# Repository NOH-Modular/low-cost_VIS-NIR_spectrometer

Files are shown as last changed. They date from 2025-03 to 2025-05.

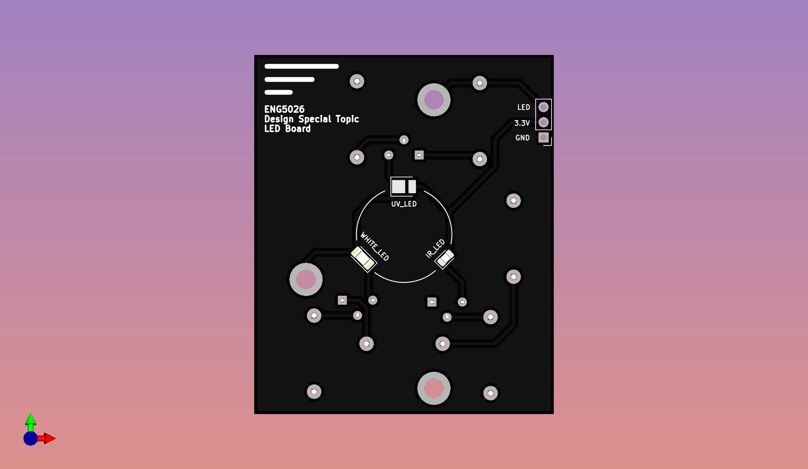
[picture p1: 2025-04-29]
HARDWARE/Embedded-Board/PICTURES/6-LED-BOARD-top.jpg

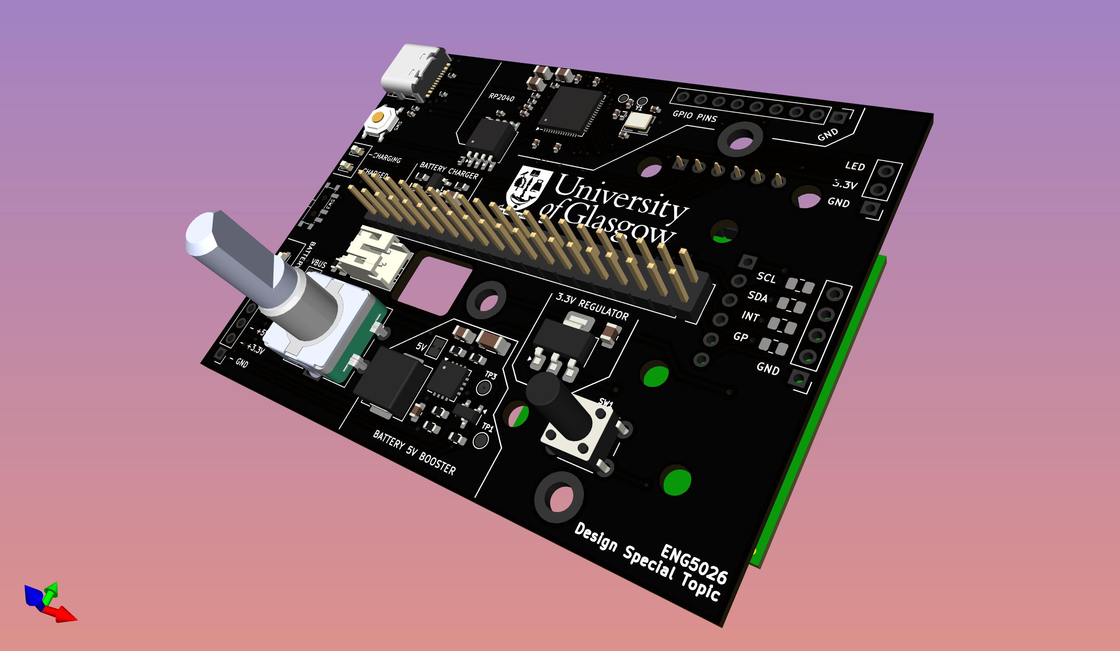
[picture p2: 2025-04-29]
HARDWARE/Embedded-Board/PICTURES/3-Embedded-Board-side.jpg

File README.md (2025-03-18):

# Low Cost VIS/NIR Spectrometer
We are a team of three students as part of Glasgow University's ENG5026 Design Special Topic 5. This class puts students in groups to initially design a proof of concept and ultimately a product in collaboration with research taking place at the University.

We aim to design a miniaturised, low-cost visible light and near-infrared spectrometer in a handheld form-factor to analyse fruit ripeness and other VIS/NIR applications including use in schools and universities. Existing products are found in the range of between £400-1000 and we aim to produce an alternative which will be more affordable and accessible.

Currently, the project consists of a custom RP2040 microcontroller board with an e-paper display to minimise power draw. The spectral sensing will use AMS-OSRAM's spectral sensor chips which has shown positive results in testing but in order to provide a more robust and elegant solution, additional funding will allow us to experiment with better sensors. The AS7265x triad sensors will give the widest possible range of sensing while still being affordable to the end user.

As well as being low-cost, it is an aim of the project to achieve long battery life for portable use. This is why low-power design such as battery management and an e-paper display has been at the forefront of component choice.

The final output (a PCB with surface-mount components pre-assembled) will be very low-cost, but we require funding for prototyping and testing various spectrometer chips, battery management, microcontrollers, and LEDs.

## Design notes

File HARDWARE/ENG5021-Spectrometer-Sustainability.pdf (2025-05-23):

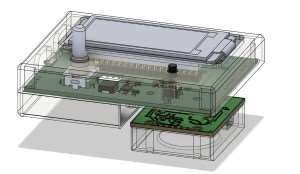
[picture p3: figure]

ENG5021-Spectrometer

3

Product name

Product life (years)

### Summary:

## Eco Audit Report

Country of use | Europe

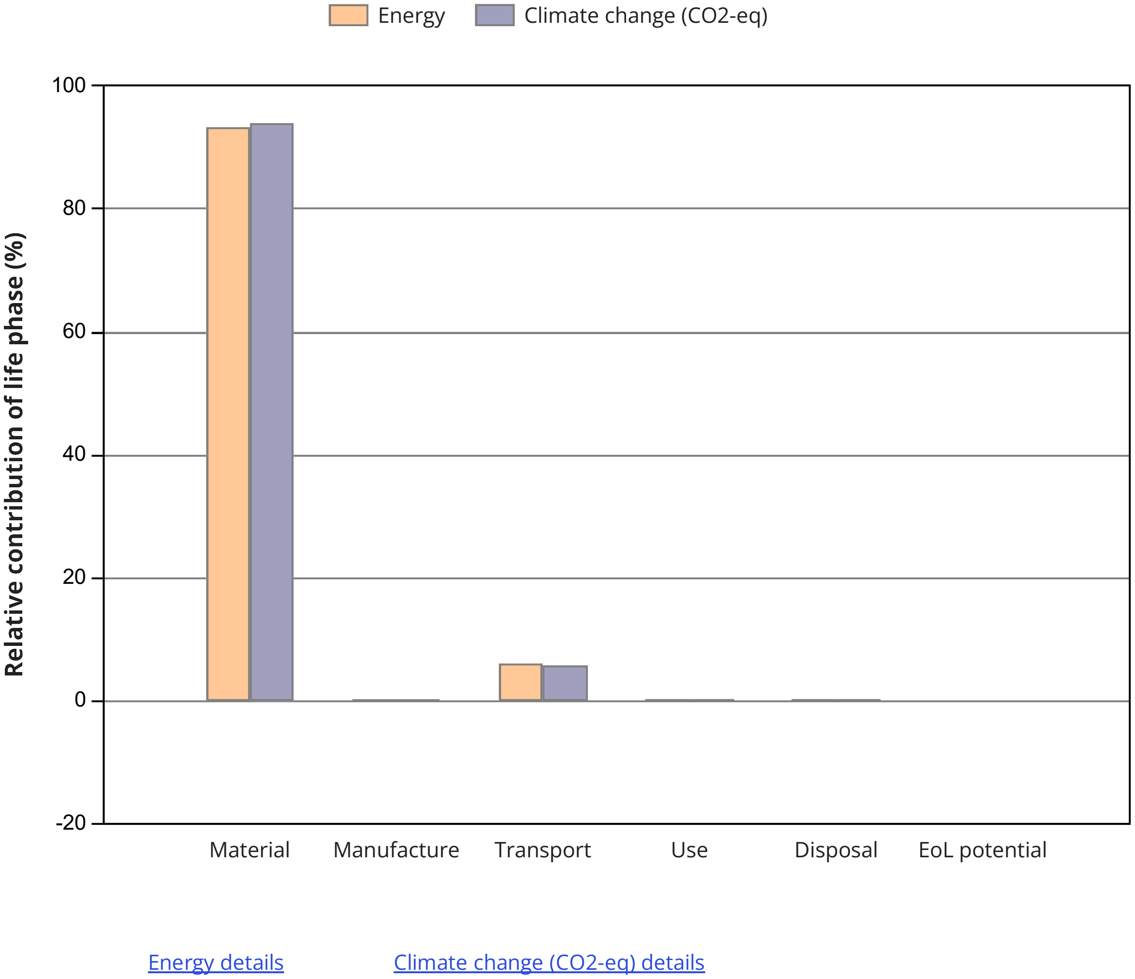
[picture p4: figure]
Material; Manufacture; Transport; Use; Disposal; EoL potential; Energy; Climate change (CO2-eq); Energy details; Climate change (CO2-eq) details

See notes on precision and data sources.

NOTE: Differences of less than 20% are not usually significant. 19-May-25

Page 1 / 10

Phase | Energy (MJ) | Energy (%) | Climate change (CO2-eq) (kg) | Climate change (CO2-eq) (%)
Material | 1.09e+03 93.5 82.3 0.148 0.0 0.0111 72.7 6.2 5.11 3.46 0.3 0.12 0.0892 0.0 0.00624 1.17e+03 100 87.6 | | | 94.0
Manufacture | | | | 0.0
Transport | | | | 5.8
Use | | | | 0.1
Disposal | | | | 0.0
Total (for first life) | | | | 100
End of life potential | 0 | | 0

Report generated by Granta EduPack 2024 R1 © 2024 ANSYS, Inc. or its

affiliated companies. All rights reserved. | 19-May-25 Page 2 / 10

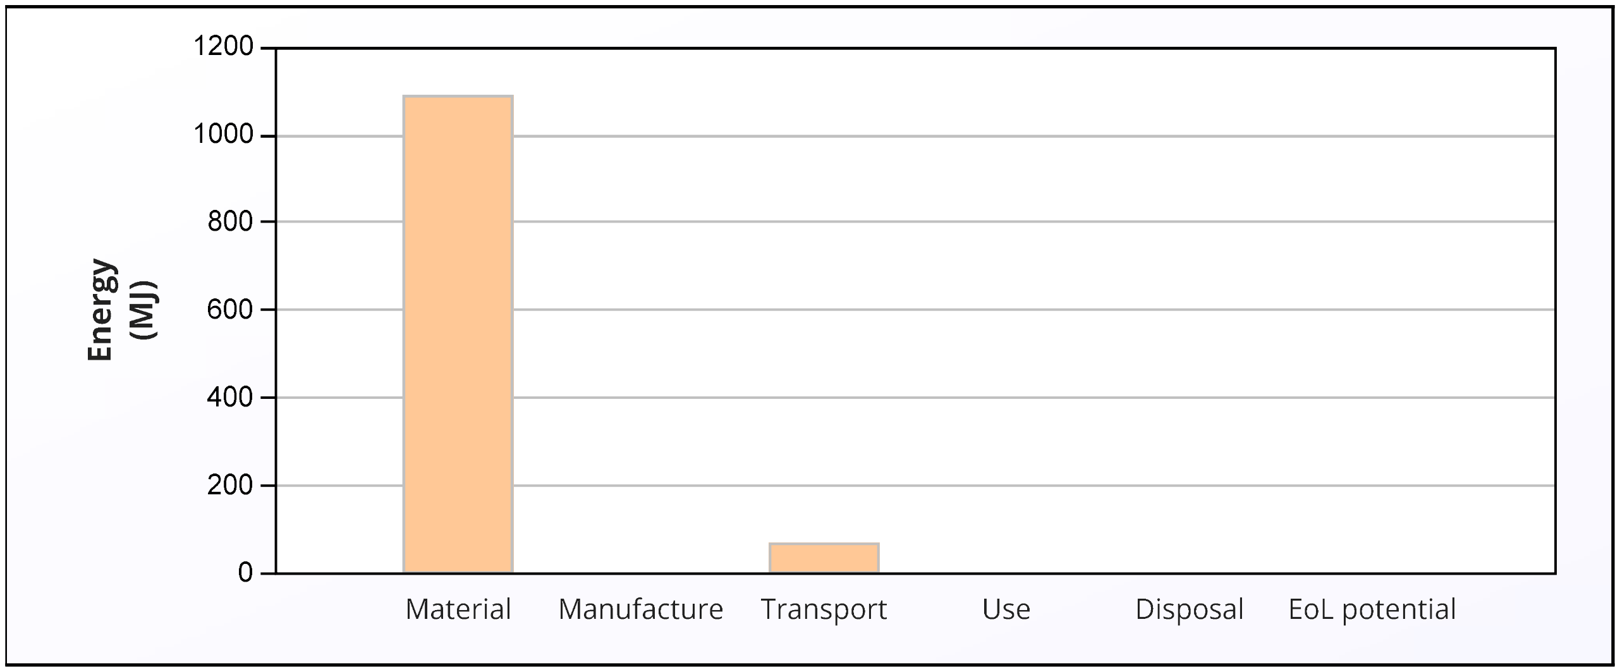
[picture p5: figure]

| Energy (MJ/year)
Equivalent annual environmental burden (averaged over 3 year product life): | 389

### Summary Energy Analysis

## Eco Audit Report

### Material:

Component | Material | Recycled content* (%) | Part mass (kg) | Qty. | Total mass (kg) | Energy (MJ) | %
Spectrometer Board | Small (hand held) electronic devices Virgin (0%) 0.3 1 0.3 8.5e+02 Small (hand held) electronic devices Virgin (0%) 0.04 1 0.04 1.1e+02 Li-Ion, rechargeable battery (for laptops) Virgin (0%) 0.016 1 0.016 15 Small (hand held) electronic devices Virgin (0%) 0.04 1 0.04 1.1e+02 PLA (general purpose) Virgin (0%) 0.025 1 0.025 1.4 | | | | | | 77.8
LED Board | | | | | | | 10.4
Rechargeable Battery | | | | | | | 1.4
Sensor PCB | | | | | | | 10.4
Plastic Enclosure | | | | | | | 0.1
Total | | | | 5 | 0.42 | 1.1e+03 | 100

## Detailed breakdown of individual life phases

Summary

*Typical: Includes 'recycle fraction in current supply'
***User-defined material

Report generated by Granta EduPack 2024 R1 © 2024 ANSYS, Inc. or its

Page 3 / 10

Manufacture: | Summary
Component | Process | Amount processed | Energy (MJ) | %
Plastic Enclosure | Polymer extrusion | 0.025 kg | 0.15 | 100.0
Total | | | 0.15 | 100

### Transport:

Breakdown by transport stage
Stage name | Transport type | Distance (km) | Energy (MJ) | %
LED/Spectrometer PCB | Aircraft, long haul belly-freight 8e+03 41 Aircraft, long haul belly-freight 6e+03 30 Truck 3.5-7.5t, EURO 3 4.4e+02 1.6 | | | 55.9
Encoder/Sensor PCB | | | | 41.9
RS - Components | | | | 2.2
Total | | 1.4e+04 | 73 | 100
Component | Mass (kg) | Energy (MJ) | %
Spectrometer Board | 0.3 52 0.04 6.9 0.016 2.8 0.04 6.9 0.025 4.3 | | 71.2
LED Board | | | 9.5
Rechargeable Battery | | | 3.9
Sensor PCB | | | 9.5
Plastic Enclosure | | | 5.9
Total | 0.42 | 73 | 100

Breakdown by components

Summary

Report generated by Granta EduPack 2024 R1 © 2024 ANSYS, Inc. or its

Page 4 / 10

### Use:

Mode | Energy
| (MJ) | %
Static | 3.5 | 100.0
Mobile | 0
Total | 3.5 | 100

Relative contribution of static and mobile modes

Energy input and output type | Electric to thermal
Country of use | Europe
Power rating (W) 0.7
Usage (hours per day) | 2
Usage (days per year) | 80
Product life (years) | 3

Static mode

Summary

### Disposal:

Component | End of life option | Energy (MJ) | %
Spectrometer Board | Landfill 0.06 Landfill 0.008 Downcycle 0.0082 Landfill 0.008 Landfill 0.005 | | 67.3
LED Board | | | 9.0
Rechargeable Battery | | | 9.2
Sensor PCB | | | 9.0
Plastic Enclosure | | | 5.6
Total | | 0.089 | 100

Summary

Component | End of life
option

Energy
(MJ) | %
Spectrometer Board | Landfill | 0
LED Board | Landfill | 0
Rechargeable Battery | Downcycle | 0
Sensor PCB | Landfill | 0
Plastic Enclosure | Landfill | 0
Total | 0 | 100

### EoL potential:

Report generated by Granta EduPack 2024 R1 © 2024 ANSYS, Inc. or its

Page 5 / 10

Notes: | Summary

Report generated by Granta EduPack 2024 R1 © 2024 ANSYS, Inc. or its

Page 6 / 10

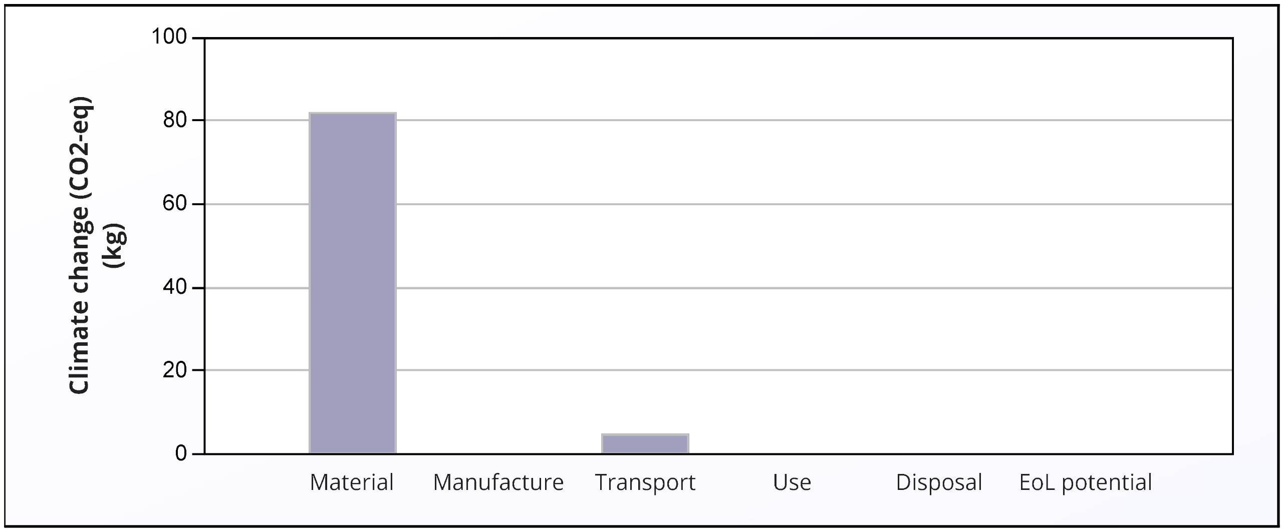
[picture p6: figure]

### Material:

Component | Material | Recycled content* (%) | Part mass (kg) | Qty. | Total mass (kg) | Climate change (CO2-eq) (kg) | %
Spectrometer Board | Small (hand held) electronic devices Virgin (0%) 0.3 1 0.3 64 Small (hand held) electronic devices Virgin (0%) 0.04 1 0.04 8.5 Li-Ion, rechargeable battery (for laptops) Virgin (0%) 0.016 1 0.016 1.7 Small (hand held) electronic devices Virgin (0%) 0.04 1 0.04 8.5 PLA (general purpose) Virgin (0%) 0.025 1 0.025 0.071 | | | | | | 77.3
LED Board | | | | | | | 10.3
Rechargeable Battery | | | | | | | 2.0
Sensor PCB | | | | | | | 10.3
Plastic Enclosure | | | | | | | 0.1
Total | | | | 5 | 0.42 | 82 | 100

## Detailed breakdown of individual life phases

Summary

*Typical: Includes 'recycle fraction in current supply'
***User-defined material
| CO2 (kg/year)
Equivalent annual environmental burden (averaged over 3 year product life): | 29.2

### Summary Climate Change (CO2-eq) Analysis

## Eco Audit Report

Report generated by Granta EduPack 2024 R1 © 2024 ANSYS, Inc. or its

Page 7 / 10

### Transport:

Breakdown by transport stage
Stage name | Transport type | Distance (km) | Climate change (CO2-eq) (kg) | %
LED/Spectrometer PCB | Aircraft, long haul belly-freight 8e+03 2.9 Aircraft, long haul belly-freight 6e+03 2.1 Truck 3.5-7.5t, EURO 3 4.4e+02 0.11 | | | 55.9
Encoder/Sensor PCB | | | | 42.0
RS - Components | | | | 2.1
Total | | 1.4e+04 | 5.1 | 100
Component | Mass (kg) | Climate change (CO2-eq) (kg) | %
Spectrometer Board | 0.3 3.6 0.04 0.49 0.016 0.2 0.04 0.49 0.025 0.3 | | 71.2
LED Board | | | 9.5
Rechargeable Battery | | | 3.9
Sensor PCB | | | 9.5
Plastic Enclosure | | | 5.9
Total | 0.42 | 5.1 | 100

Breakdown by components

Summary

Manufacture: | Summary
Component | Process | Amount processed | Climate change (CO2-eq) (kg) | %
Plastic Enclosure | Polymer extrusion | 0.025 kg | 0.011 | 100.0
Total | | | 0.011 | 100

Report generated by Granta EduPack 2024 R1 © 2024 ANSYS, Inc. or its

Page 8 / 10

### Disposal:

Component | End of life option | Climate change (CO2-eq) (kg) | %
Spectrometer Board | Landfill 0.0042 Landfill 0.00056 Downcycle 0.00057 Landfill 0.00056 Landfill 0.00035 | | 67.3
LED Board | | | 9.0
Rechargeable Battery | | | 9.2
Sensor PCB | | | 9.0
Plastic Enclosure | | | 5.6
Total | | 0.0062 | 100

Summary

Component | End of life
option

Climate
change
(CO2-eq)
(kg)

%

Spectrometer Board | Landfill | 0
LED Board | Landfill | 0
Rechargeable Battery | Downcycle | 0
Sensor PCB | Landfill | 0
Plastic Enclosure | Landfill | 0
Total | 0 | 100

### EoL potential:

### Use:

Mode | Climate change (CO2-eq)
| (kg) | %
Static | 0.12 | 100.0
Mobile | 0
Total | 0.12 | 100

Relative contribution of static and mobile modes

Energy input and output type | Electric to thermal
Country of use | Europe
Power rating (W) 0.7
Usage (hours per day) | 2
Usage (days per year) | 80
Product life (years) | 3

Static mode

Summary

Report generated by Granta EduPack 2024 R1 © 2024 ANSYS, Inc. or its

Page 9 / 10

Notes: | Summary

Report generated by Granta EduPack 2024 R1 © 2024 ANSYS, Inc. or its

Page 10 / 10

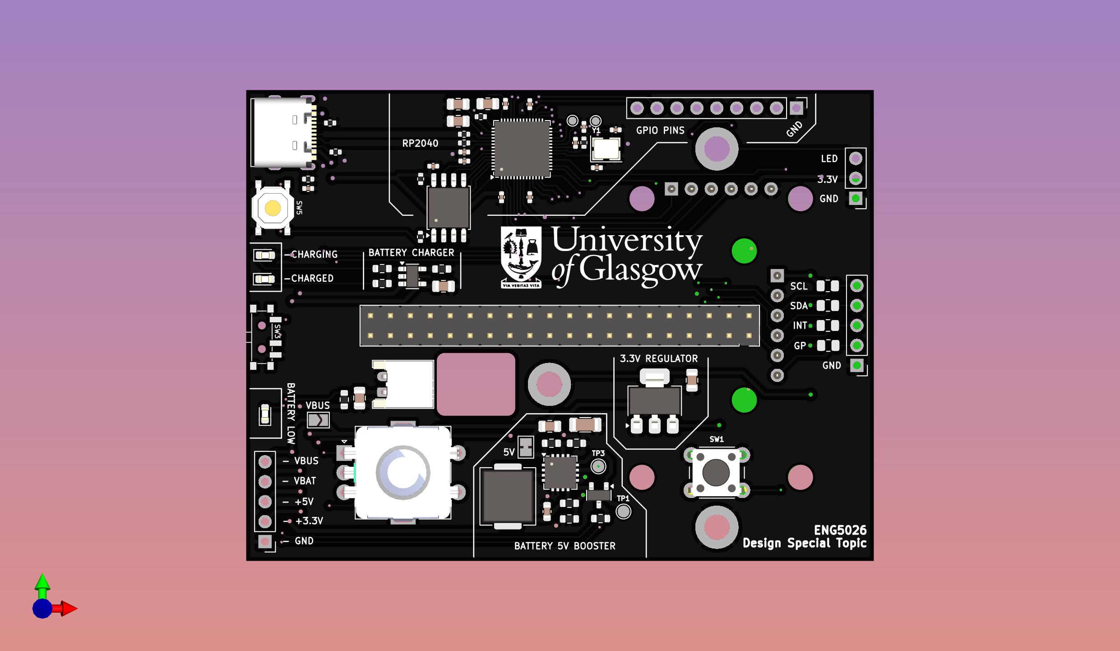
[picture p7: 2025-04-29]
HARDWARE/Embedded-Board/PICTURES/1-Embedded-Board-top.jpg

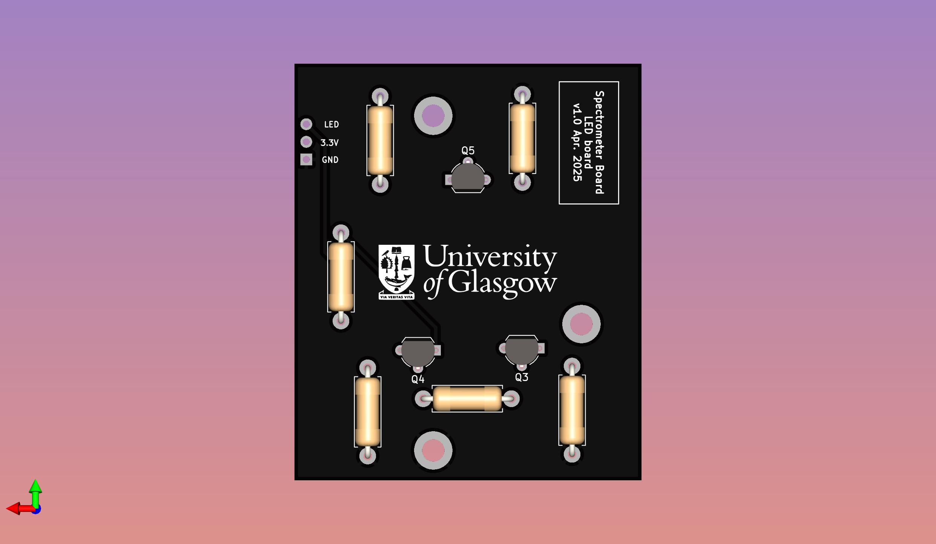
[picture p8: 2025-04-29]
HARDWARE/Embedded-Board/PICTURES/4-LED-BOARD-bottom.jpg

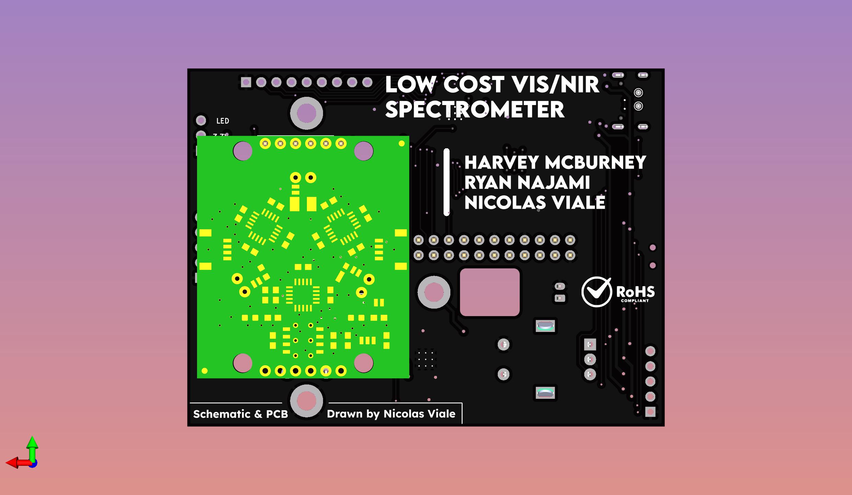
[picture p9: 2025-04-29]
HARDWARE/Embedded-Board/PICTURES/2-Embedded-Board-bottom.jpg

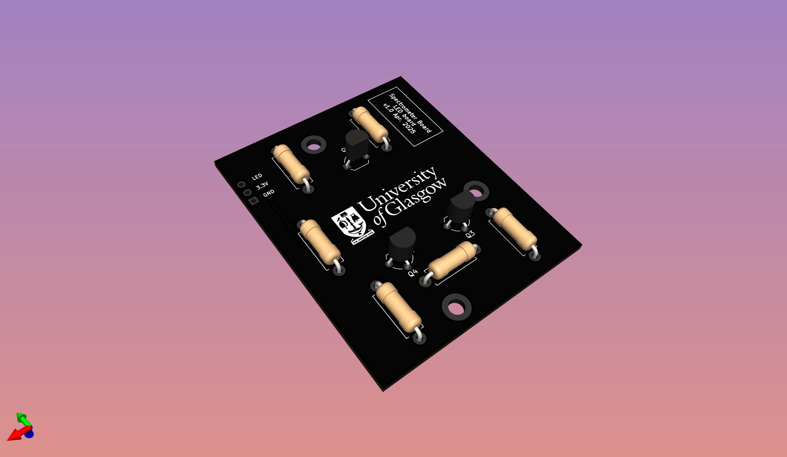
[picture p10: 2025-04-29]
HARDWARE/Embedded-Board/PICTURES/5-LED-BOARD-side.jpg

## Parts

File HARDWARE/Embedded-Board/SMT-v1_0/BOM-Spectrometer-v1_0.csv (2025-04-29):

Comment | Designator | Footprint | LCSC Part Number
Battery_Cell | BT1 | Connector_JST:JST_PH_S2B-PH-K_1x02_P2.00mm_Horizontal | C5359610
100n | C4 | Capacitor_SMD:C_0603_1608Metric | C14663
100u/6V | C6 | Capacitor_SMD:C_1206_3216Metric | C15008
10u | C2,C3,C58 | Capacitor_SMD:C_0805_2012Metric | C15850
USB_C_Receptacle_USB2.0 | J11 | userr:USB-C-JLCPCB | C165948
6.8u | L1 | Inductor_SMD:L_APV_APH0630 | C5349706
MMUN2133LT1G | Q1 | Package_TO_SOT_SMD:SOT-23 | C86182
10k | R3 | Resistor_SMD:R_0402_1005Metric | C25744
470 | R6 | Resistor_SMD:R_0603_1608Metric | C23179
200 | R7 | Resistor_SMD:R_0402_1005Metric | C25087
2k | R9 | Resistor_SMD:R_0603_1608Metric | C22975
220 | R12 | Resistor_SMD:R_0402_1005Metric | C25091
200k | R19 | Resistor_SMD:R_0603_1608Metric | C25811
SW_Push_SPDT | SW3 | userr:Alps-Alpine-SPDT | C109335
BOOT | SW5 | userr:JLC-BASIC-BUTTON | C318884
MCP73831-2-OT | U1 | Package_TO_SOT_SMD:SOT-23-5 | C424093
W25Q16JVS | U2 | Package_SO:SOIC-8_5.3x5.3mm_P1.27mm | C97521
RP2040 | U3 | Package_DFN_QFN:QFN-56-1EP_7x7mm_P0.4mm_EP3.2x3.2mm | C2040
TPS61090 | U4 | Package_DFN_QFN:Texas_RSA_VQFN-16-1EP_4x4mm_P0.65mm_EP2.7x2.7mm_ThermalVias | C206167
LM1117-3.3 | U18 | Package_TO_SOT_SMD:SOT-223-3_TabPin2 | C6186
12MHz | Y1 | Crystal:Crystal_SMD_3225-4Pin_3.2x2.5mm | C9002
33p | C48,C68 | Capacitor_SMD:C_0402_1005Metric | C1562
1k | R4,R5 | Resistor_SMD:R_0402_1005Metric | C11702
1k | R8,R20 | Resistor_SMD:R_0603_1608Metric | C21190
1.85M | R10,R18 | Resistor_SMD:R_0603_1608Metric | C325651
340k | R11,R17 | Resistor_SMD:R_0603_1608Metric | C23143
5.1k | R13,R14 | Resistor_SMD:R_0402_1005Metric | C25905
27 | R15,R16 | Resistor_SMD:R_0402_1005Metric | C138021
2.2u | C5,C13,C14,C21 | Capacitor_SMD:C_0805_2012Metric | C377773
100n | C8,C11,C12,C15,C16,C17,C18,C19,C20,C34 | Capacitor_SMD:C_0402_1005Metric | C307331

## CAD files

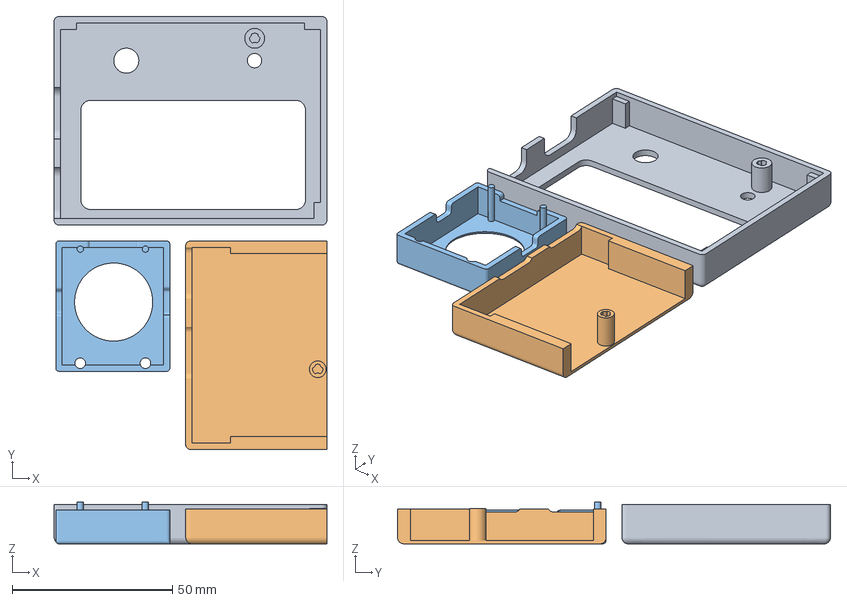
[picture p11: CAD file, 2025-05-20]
3D-Case/embedded-case-top-v1.3mf
85.0 x 134.9 x 13.0 mm
embedded-case-top-v1.stl
embedded-case-bottom-v1.stl
embedded-case-sensor-v1.stl

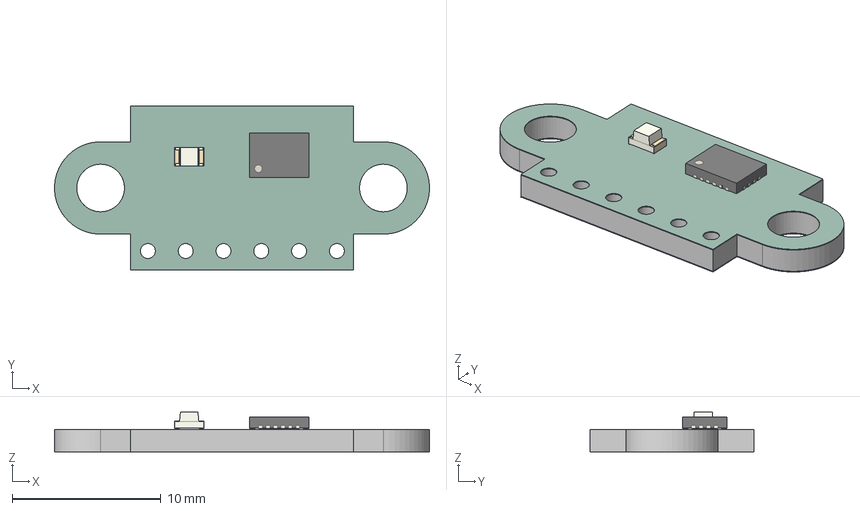
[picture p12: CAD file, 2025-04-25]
HARDWARE/Embedded-Board/3D-files/AS7341.step
25.2 x 11.0 x 2.75 mm
LED_0805_2012Metric
QFN-20-1EP_3x4mm_P0.5mm_EP1.65x2.65mm
AS7341_soldermask
AS7341_PCB

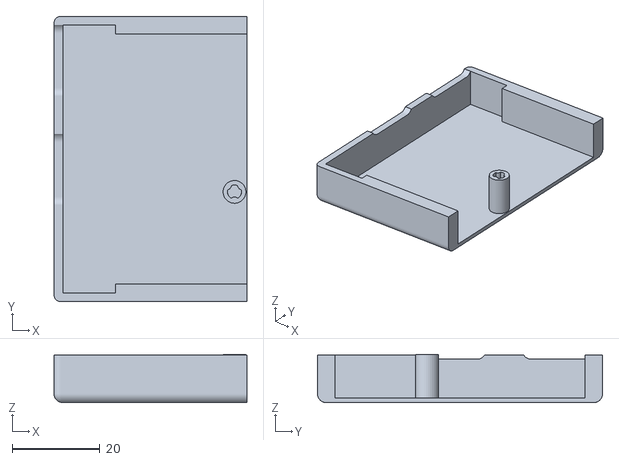
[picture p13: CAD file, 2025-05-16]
3D-Case/embedded-case-bottom-v1.stl
44.0 x 65.0 x 11.0

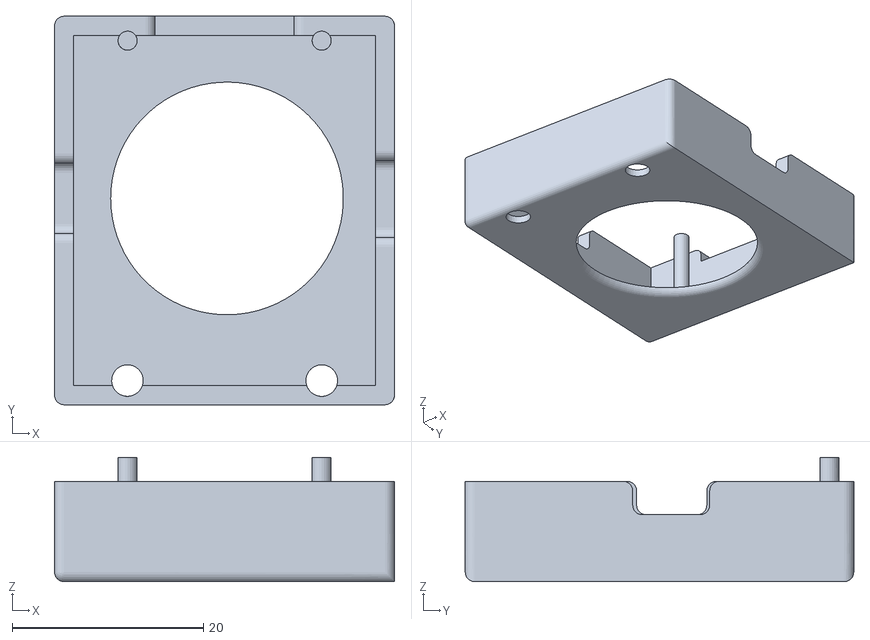
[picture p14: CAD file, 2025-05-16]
3D-Case/embedded-case-sensor-v1.stl
35.6 x 40.6 x 13.0

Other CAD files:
3D-Case/embedded-case-top-v1.stl

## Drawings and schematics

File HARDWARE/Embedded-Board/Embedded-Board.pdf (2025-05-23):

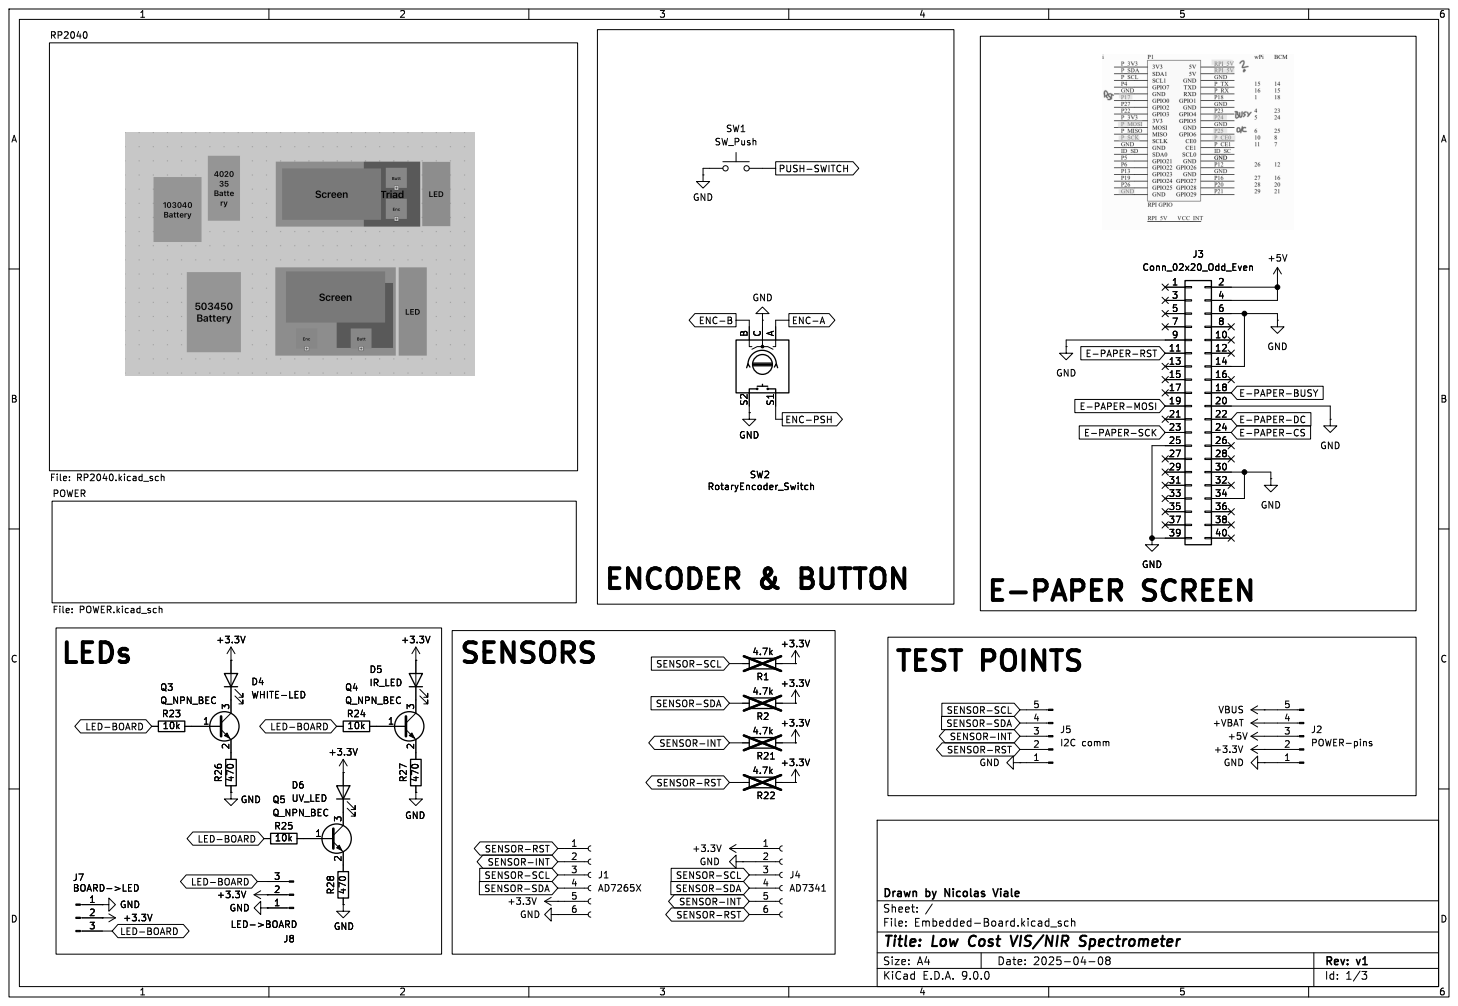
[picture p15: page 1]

A S2S1 SW2 RotaryEncoder_Switch GND GND GND GND GND

E-PAPER-MOSI LED-BOARD

SENSOR-INT SENSOR-SCL SENSOR-RST SENSOR-RST SENSOR-SCL SENSOR-SDA

SENSOR-INT SENSOR-SDA

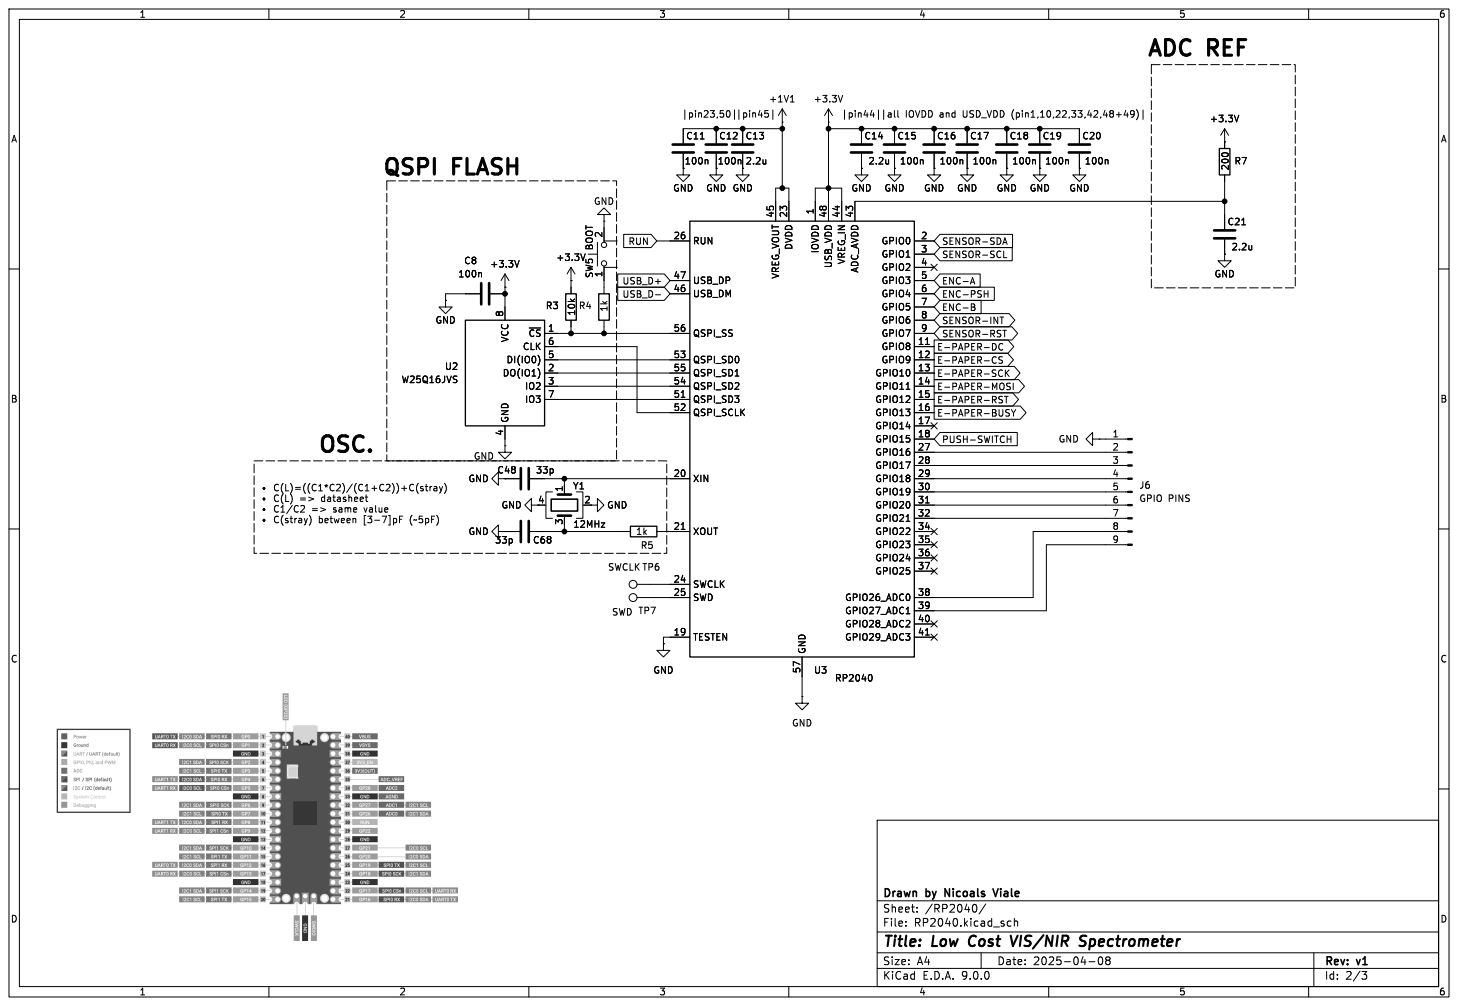
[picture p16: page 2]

ENC-PSH
SENSOR-INT SENSOR-RST ENC-B

þÿ "C(L)=((C1*C2)/(C1+C2))+C(stray)
þÿ "C(L) => datasheet þÿ "C1/C2 => same value

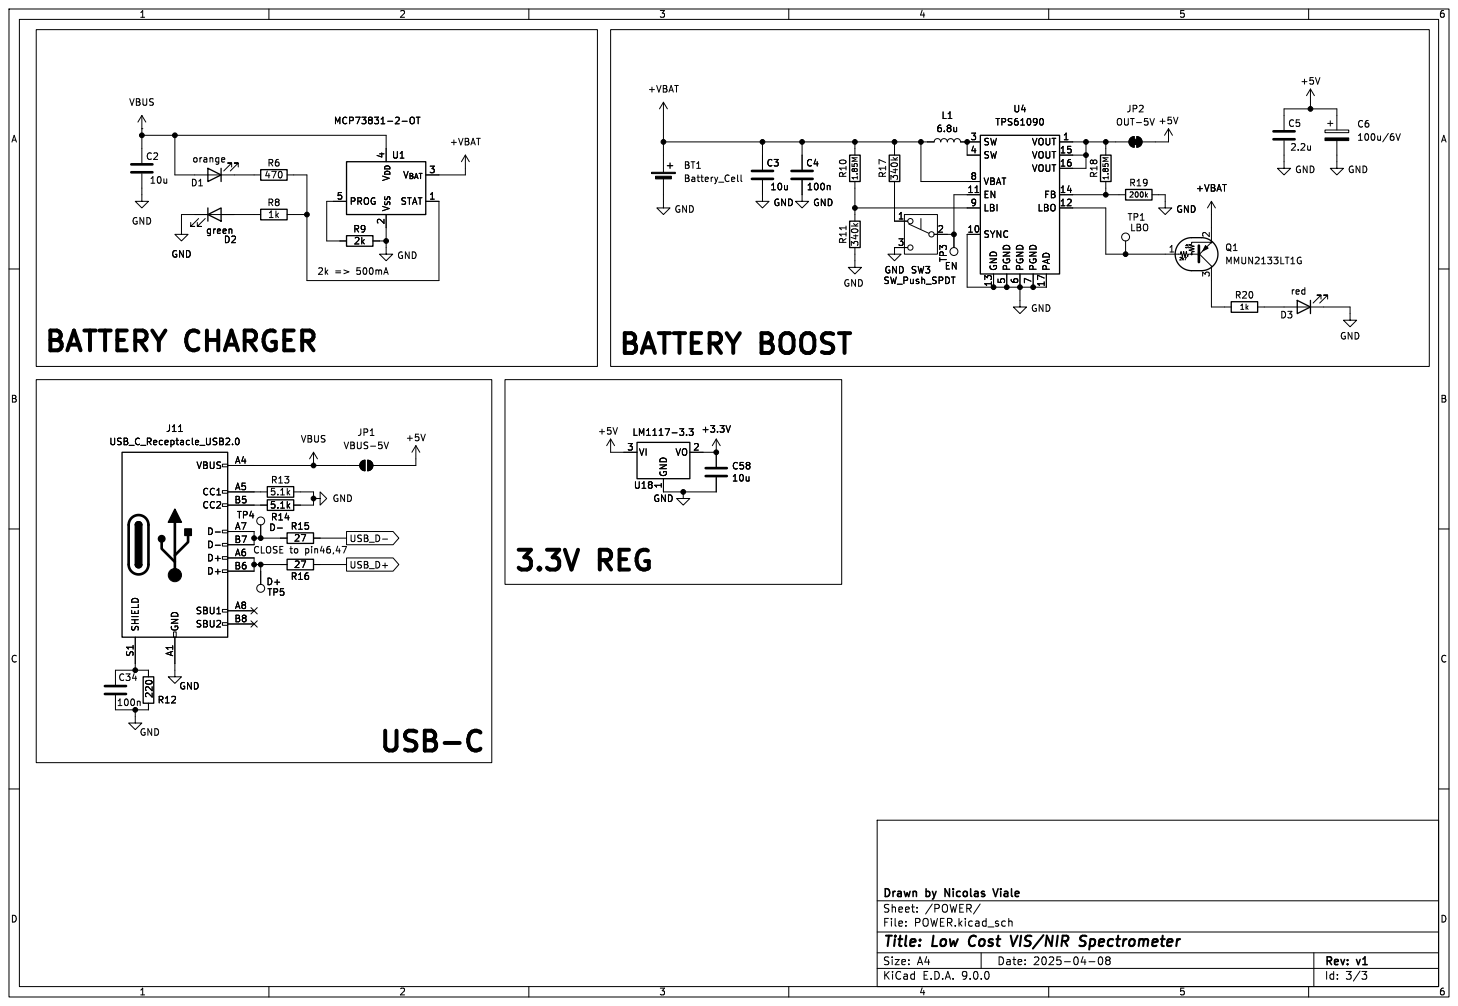
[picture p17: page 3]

7 PAD 17 VOUT 1 VOUT 15 VOUT 16 FB 14

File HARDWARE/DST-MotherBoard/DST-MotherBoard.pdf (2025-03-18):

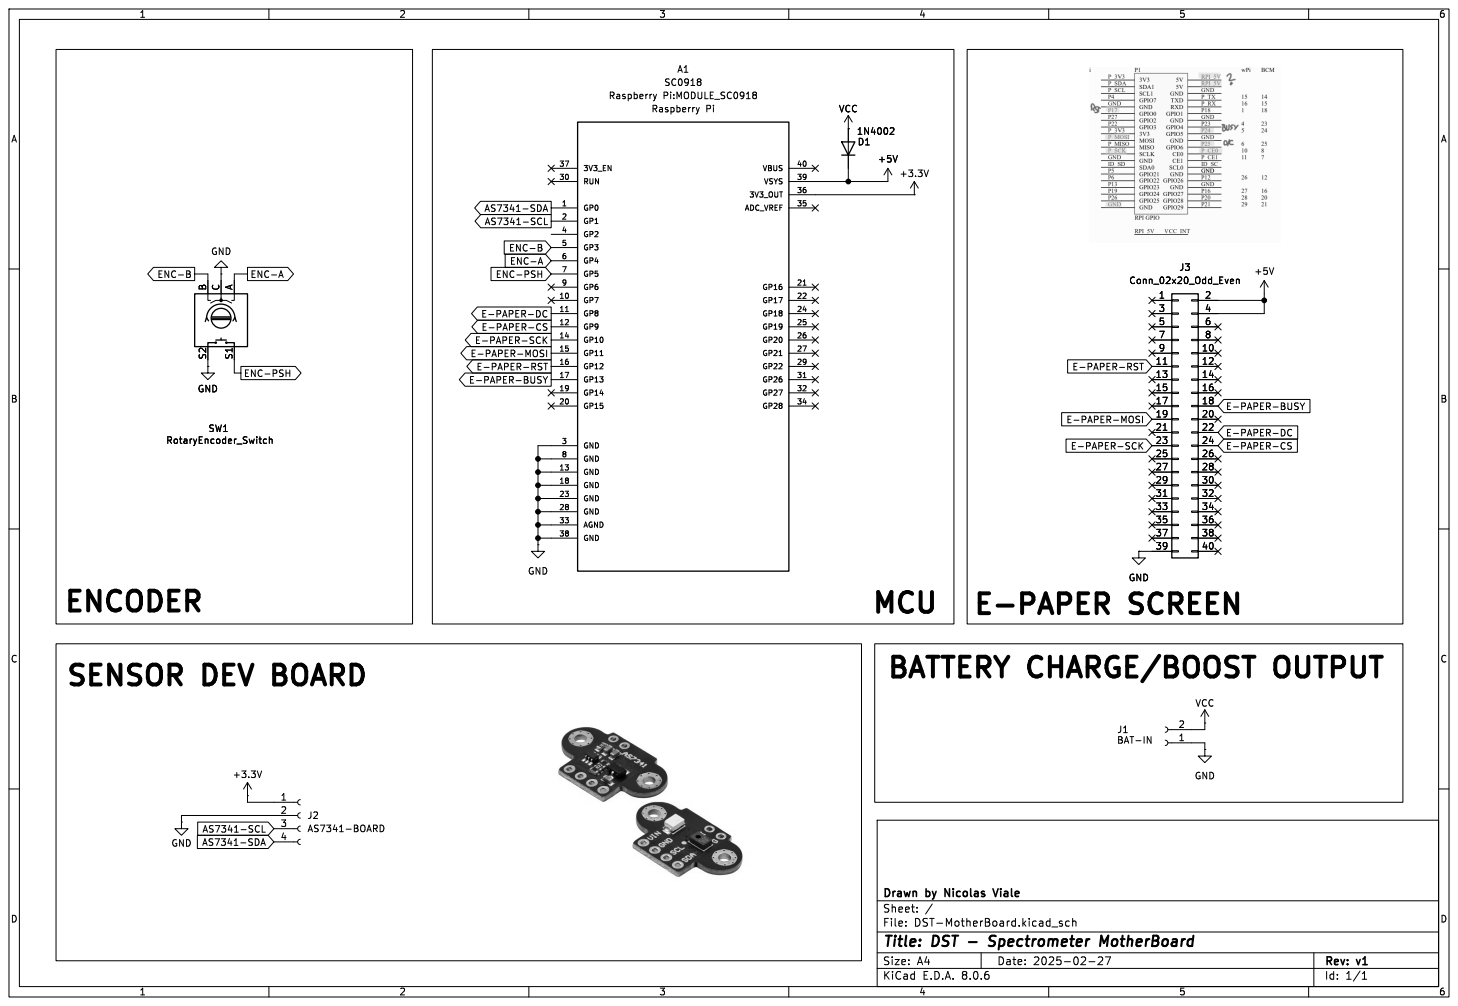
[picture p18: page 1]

E-PAPER-RST E-PAPER-MOSI E-PAPER-SCK

Id: 1/1 Title: DST - Spectrometer MotherBoard

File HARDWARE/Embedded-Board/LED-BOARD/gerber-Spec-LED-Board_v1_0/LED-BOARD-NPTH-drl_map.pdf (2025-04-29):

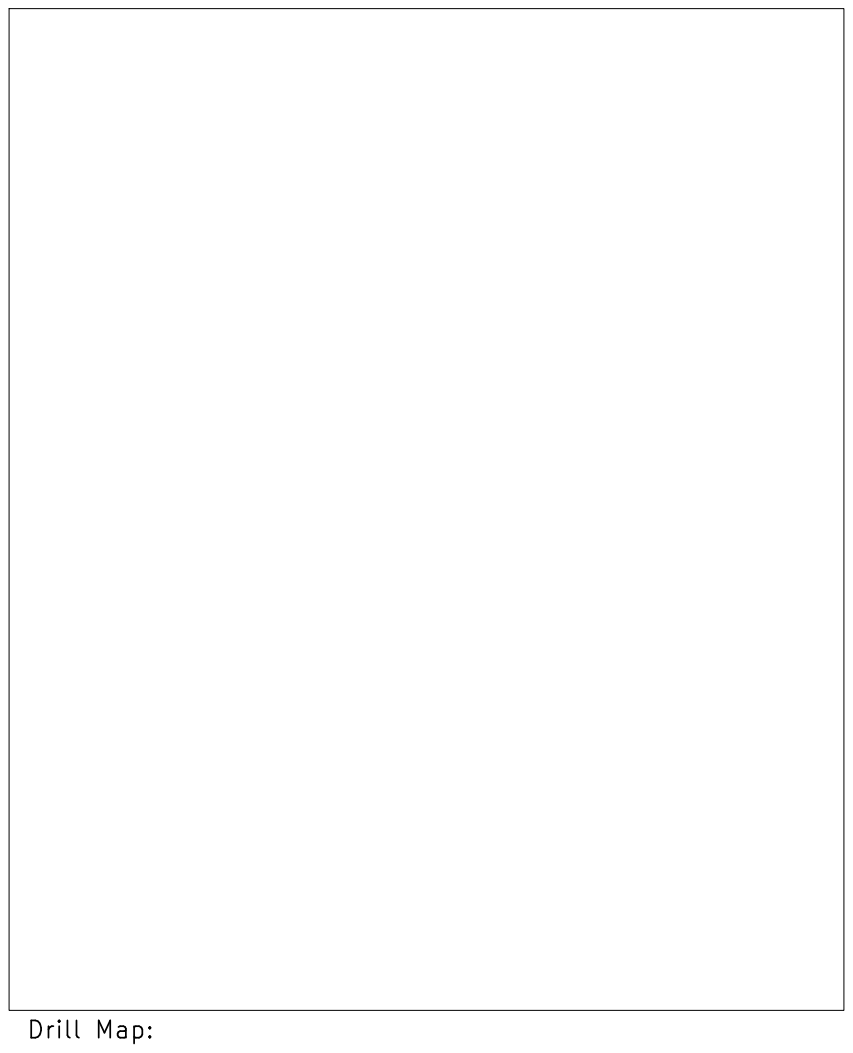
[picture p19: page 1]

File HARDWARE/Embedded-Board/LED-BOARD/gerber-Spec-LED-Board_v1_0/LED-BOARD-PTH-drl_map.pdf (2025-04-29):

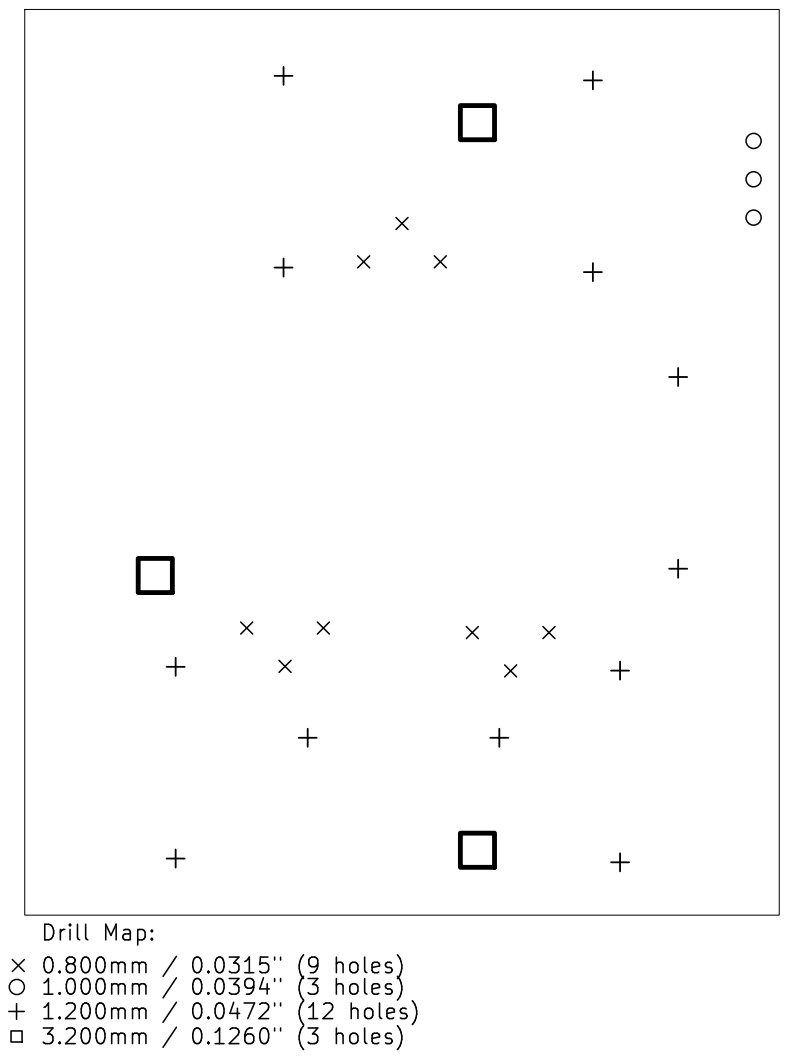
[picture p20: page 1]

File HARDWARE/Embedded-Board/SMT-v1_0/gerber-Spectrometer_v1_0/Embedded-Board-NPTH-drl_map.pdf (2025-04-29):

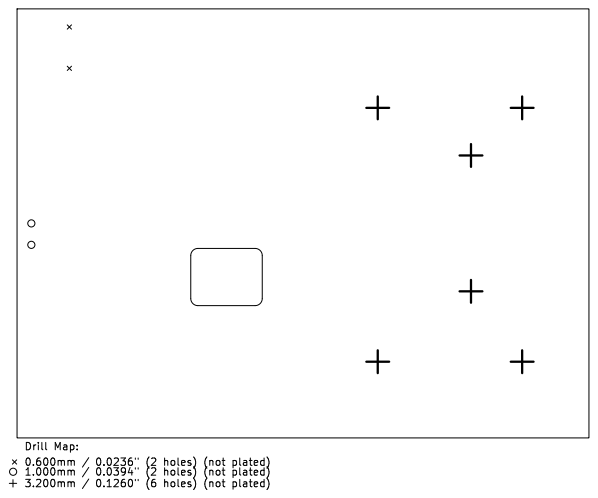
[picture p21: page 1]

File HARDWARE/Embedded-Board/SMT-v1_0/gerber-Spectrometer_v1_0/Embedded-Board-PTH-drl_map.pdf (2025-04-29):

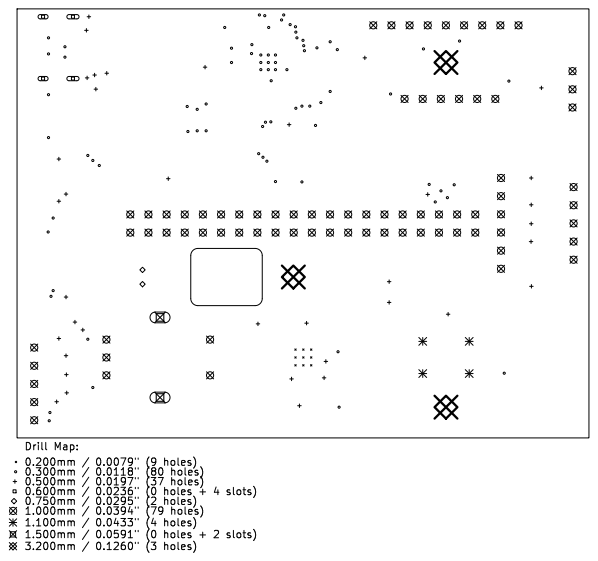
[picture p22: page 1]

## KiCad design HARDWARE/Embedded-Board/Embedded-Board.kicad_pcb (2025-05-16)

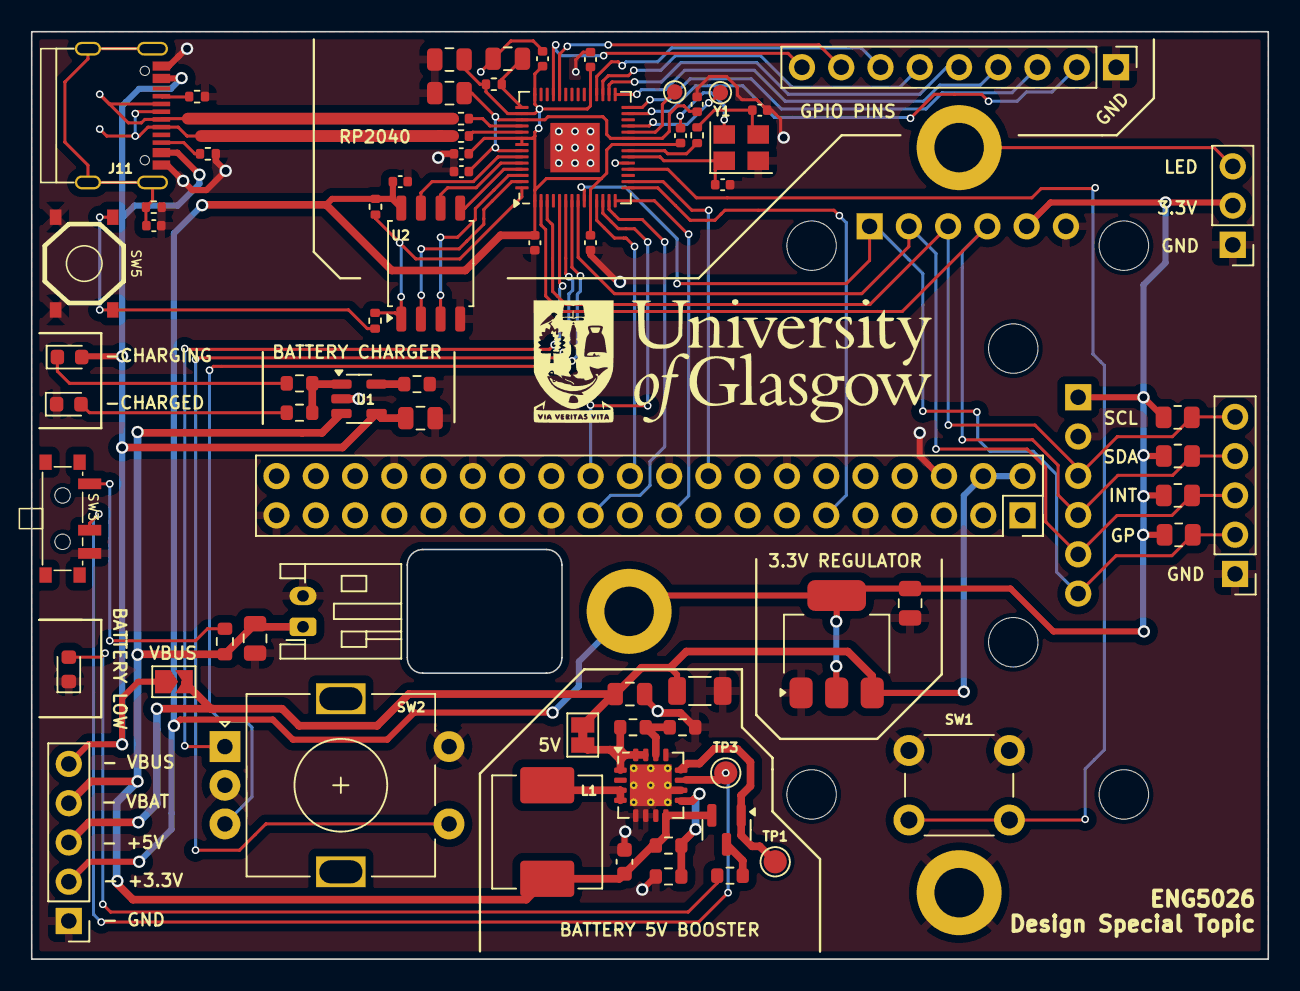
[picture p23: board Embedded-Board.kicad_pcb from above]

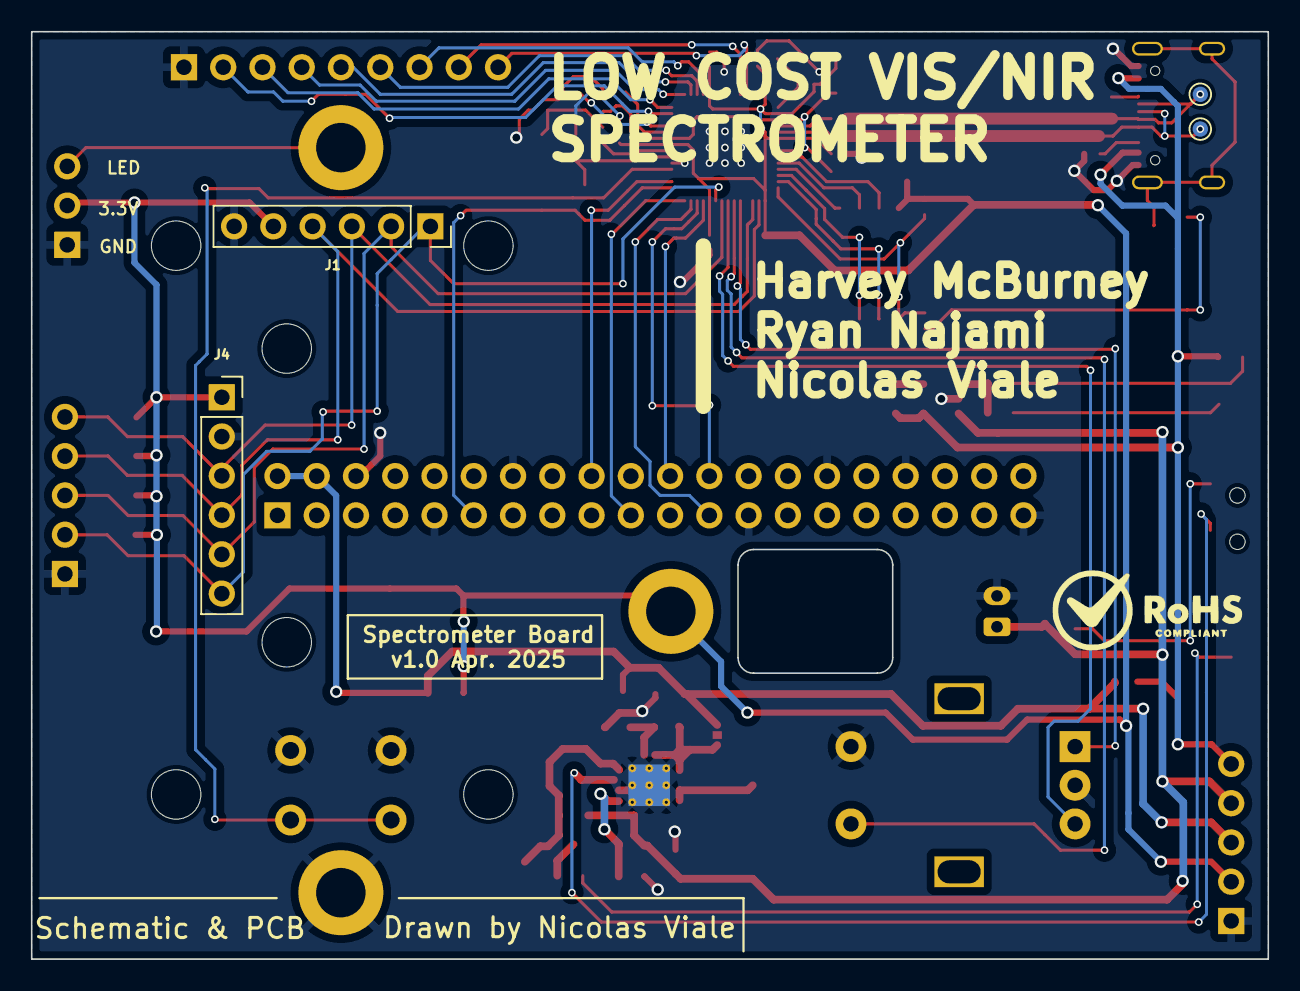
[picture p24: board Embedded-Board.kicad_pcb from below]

Board: 2 copper layers, 80.0 x 60.0 mm, 75 parts (4 on the bottom side), 61 nets.

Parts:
BT1: Battery_Cell; JST_PH_S2B-PH-K_1x02_P2.00mm_Horizontal
C2, C3, C58: 10u; C_0805_2012Metric
C4: 100n; C_0603_1608Metric
C5, C13, C14, C21: 2.2u; C_0805_2012Metric
C6: 100u/6V; C_1206_3216Metric
C8, C11, C12, C15, C16, C17, C18, C19, C20, C34: 100n; C_0402_1005Metric
C48, C68: 33p; C_0402_1005Metric
D1: orange; LED_0603_1608Metric
D2: green; LED_0603_1608Metric
D3: red; LED_0603_1608Metric
J1: AD7265X; PinSocket_1x06_P2.54mm_Vertical
J2: POWER-pins; PinHeader_1x05_P2.54mm_Vertical
J3: Conn_02x20_Odd_Even; PinSocket_2x20_P2.54mm_Vertical
J4: AD7341; PinSocket_1x06_P2.54mm_Vertical
J5: I2C comm; PinHeader_1x05_P2.54mm_Vertical
J6: GPIO PINS; PinHeader_1x09_P2.54mm_Vertical
J7: BOARD->LED; PinHeader_1x03_P2.54mm_Vertical
J11: USB_C_Receptacle_USB2.0; USB-C-JLCPCB
JP1: VBUS-5V; SolderJumper-2_P1.3mm_Open_TrianglePad1.0x1.5mm
JP2: OUT-5V; SolderJumper-2_P1.3mm_Bridged_Pad1.0x1.5mm
L1: 6.8u; L_APV_APH0630
Q1: MMUN2133LT1G; SOT-23
R1, R2, R21, R22: 4.7k; R_0805_2012Metric
R3: 10k; R_0402_1005Metric
R4, R5: 1k; R_0402_1005Metric
R6: 470; R_0603_1608Metric
R7: 200; R_0402_1005Metric
R8, R20: 1k; R_0603_1608Metric
R9: 2k; R_0603_1608Metric
R10, R18: 1.85M; R_0603_1608Metric
R11, R17: 340k; R_0603_1608Metric
R12: 220; R_0402_1005Metric
R13, R14: 5.1k; R_0402_1005Metric
R15, R16: 27; R_0402_1005Metric
R19: 200k; R_0603_1608Metric
SW1: SW_Push; SW_PUSH_6mm_H13mm
SW2: RotaryEncoder_Switch; RotaryEncoder_Alps_EC11E-Switch_Vertical_H20mm
SW3: SW_Push_SPDT; Alps-Alpine-SPDT
SW5: BOOT; JLC-BASIC-BUTTON
TP1: LBO; TestPoint_Pad_D1.5mm
TP3: EN; TestPoint_Pad_D1.5mm
TP4: D-; TestPoint_Pad_D1.0mm
TP5: D+; TestPoint_Pad_D1.0mm
TP6: SWCLK; TestPoint_Pad_D1.0mm
TP7: SWD; TestPoint_Pad_D1.0mm
U1: MCP73831-2-OT; SOT-23-5
U2: W25Q16JVS; SOIC-8_5.3x5.3mm_P1.27mm
U3: RP2040; QFN-56-1EP_7x7mm_P0.4mm_EP3.2x3.2mm
U4: TPS61090; Texas_RSA_VQFN-16-1EP_4x4mm_P0.65mm_EP2.7x2.7mm_ThermalVias
U18: LM1117-3.3; SOT-223-3_TabPin2
Y1: 12MHz; Crystal_SMD_3225-4Pin_3.2x2.5mm

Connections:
+1V1: C11.1, C12.1, C13.1, U3.23 (DVDD), U3.45 (VREG_VOUT), U3.50 (DVDD)
+3.3V: C8.1, C14.1, C15.1, C16.1, C17.1, C18.1, C19.1, C20.1, C58.1, J1.5, J2.2, J4.1, J7.2, R1.1, R2.1, R3.1, R7.1, R21.1, R22.1, U2.8 (VCC), U3.1 (IOVDD), U3.10 (IOVDD), U3.22 (IOVDD), U3.33 (IOVDD), U3.42 (IOVDD), U3.44 (VREG_IN), U3.48 (USB_VDD), U3.49 (IOVDD), U18.2 (VO)
+5V: C5.1, C6.1, J2.3, J3.2, J3.4, JP1.2 (B), JP2.2 (B), U18.3 (VI)
+VBAT: BT1.1 (+), C3.1, C4.1, J2.4, L1.1, Q1.2 (E), R10.2, R17.2, U1.3 (V_{BAT}), U4.8 (VBAT)
E-PAPER-BUSY: J3.18, U3.16 (GPIO13)
E-PAPER-CS: J3.24, U3.12 (GPIO9)
E-PAPER-DC: J3.22, U3.11 (GPIO8)
E-PAPER-MOSI: J3.19, U3.14 (GPIO11)
E-PAPER-RST: J3.11, U3.15 (GPIO12)
E-PAPER-SCK: J3.23, U3.13 (GPIO10)
ENC-A: SW2.A, U3.5 (GPIO3)
ENC-B: SW2.B, U3.7 (GPIO5)
ENC-PSH: SW2.S1, U3.6 (GPIO4)
GND: BT1.2 (-), C2.2, C3.2, C4.2, C5.2, C6.2, C8.2, C11.2, C12.2, C13.2, C14.2, C15.2, C16.2, C17.2, C18.2, C19.2, C20.2, C21.2, C34.2, C48.1, C58.2, C68.2, D2.1 (K), D3.1 (K), J1.6, J2.1, J3.6, J3.9, J3.14, J3.20, J3.25, J3.30, J3.34, J3.39, J4.2, J5.1, J6.1, J7.1, J11.A1 (GND), J11.B1 (GND), R9.2, R11.1, R12.2, R13.2, R14.1, R19.2, SW1.1, SW2.C, SW2.S2, SW3.3 (C), SW5.2, U1.2 (V_{SS}), U2.4 (GND), U3.19 (TESTEN), U3.57 (GND), U4.5 (PGND), U4.6 (PGND), U4.7 (PGND), U4.10 (SYNC), U4.13 (GND), U4.17 (PAD), U18.1 (GND), Y1.2, Y1.4
unnamed: C68.1, R5.1, Y1.3
unnamed: D1.1 (K), R6.1
unnamed: D2.2 (A), R8.1
unnamed: D3.2 (A), R20.2
unnamed: J6.2, U3.27 (GPIO16)
unnamed: J6.3, U3.28 (GPIO17)
unnamed: J6.4, U3.29 (GPIO18)
unnamed: J6.5, U3.30 (GPIO19)
unnamed: J6.6, U3.31 (GPIO20)
unnamed: J6.7, U3.32 (GPIO21)
unnamed: J6.8, U3.38 (GPIO26_ADC0)
unnamed: J6.9, U3.39 (GPIO27_ADC1)
unnamed: J11.A5 (CC1), R13.1
unnamed: J11.B5 (CC2), R14.2
unnamed: J11.A6 (D+), J11.B6 (D+), R16.2, TP5.1
unnamed: J11.A7 (D-), J11.B7 (D-), R15.1, TP4.1
unnamed: C34.1, J11.S1 (SHIELD), R12.1
unnamed: JP2.1 (A), R18.2, U4.1 (VOUT), U4.15 (VOUT), U4.16 (VOUT)
unnamed: L1.2, U4.3 (SW), U4.4 (SW)
unnamed: Q1.1 (B), TP1.1, U4.12 (LBO)
unnamed: Q1.3 (C), R20.1
unnamed: R4.1, SW5.1
unnamed: R17.1, SW3.1 (A)
unnamed: SW3.2 (B), TP3.1, U4.11 (EN)
unnamed: R9.1, U1.5 (PROG)
unnamed: R6.2, R8.2, U1.1 (STAT)
unnamed: U2.6 (CLK), U3.52 (QSPI_SCLK)
unnamed: U2.5 (DI(IO0)), U3.53 (QSPI_SD0)
unnamed: U2.2 (DO(IO1)), U3.55 (QSPI_SD1)
unnamed: U2.3 (IO2), U3.54 (QSPI_SD2)
unnamed: U2.7 (IO3), U3.51 (QSPI_SD3)
unnamed: R3.2, R4.2, U2.1 (~CS), U3.56 (QSPI_SS)
unnamed: C21.1, R7.2, U3.43 (ADC_AVDD)
unnamed: TP6.1, U3.24 (SWCLK)
unnamed: TP7.1, U3.25 (SWD)
unnamed: C48.2, U3.20 (XIN), Y1.1
unnamed: R5.2, U3.21 (XOUT)
unnamed: R18.1, R19.1, U4.14 (FB)
unnamed: R10.1, R11.2, U4.9 (LBI)
PUSH-SWITCH: SW1.2, U3.18 (GPIO15)
SENSOR-INT: J1.2, J4.5, J5.3, R21.2, U3.8 (GPIO6)
SENSOR-RST: J1.1, J4.6, J5.2, R22.2, U3.9 (GPIO7)
SENSOR-SCL: J1.3, J4.3, J5.5, R1.2, U3.3 (GPIO1)
SENSOR-SDA: J1.4, J4.4, J5.4, R2.2, U3.2 (GPIO0)
USB_D+: R16.1, U3.47 (USB_DP)
USB_D-: R15.2, U3.46 (USB_DM)
VBUS: C2.1, D1.2 (A), J2.5, J11.A4 (VBUS), J11.B4 (VBUS), JP1.1 (A), U1.4 (V_{DD})

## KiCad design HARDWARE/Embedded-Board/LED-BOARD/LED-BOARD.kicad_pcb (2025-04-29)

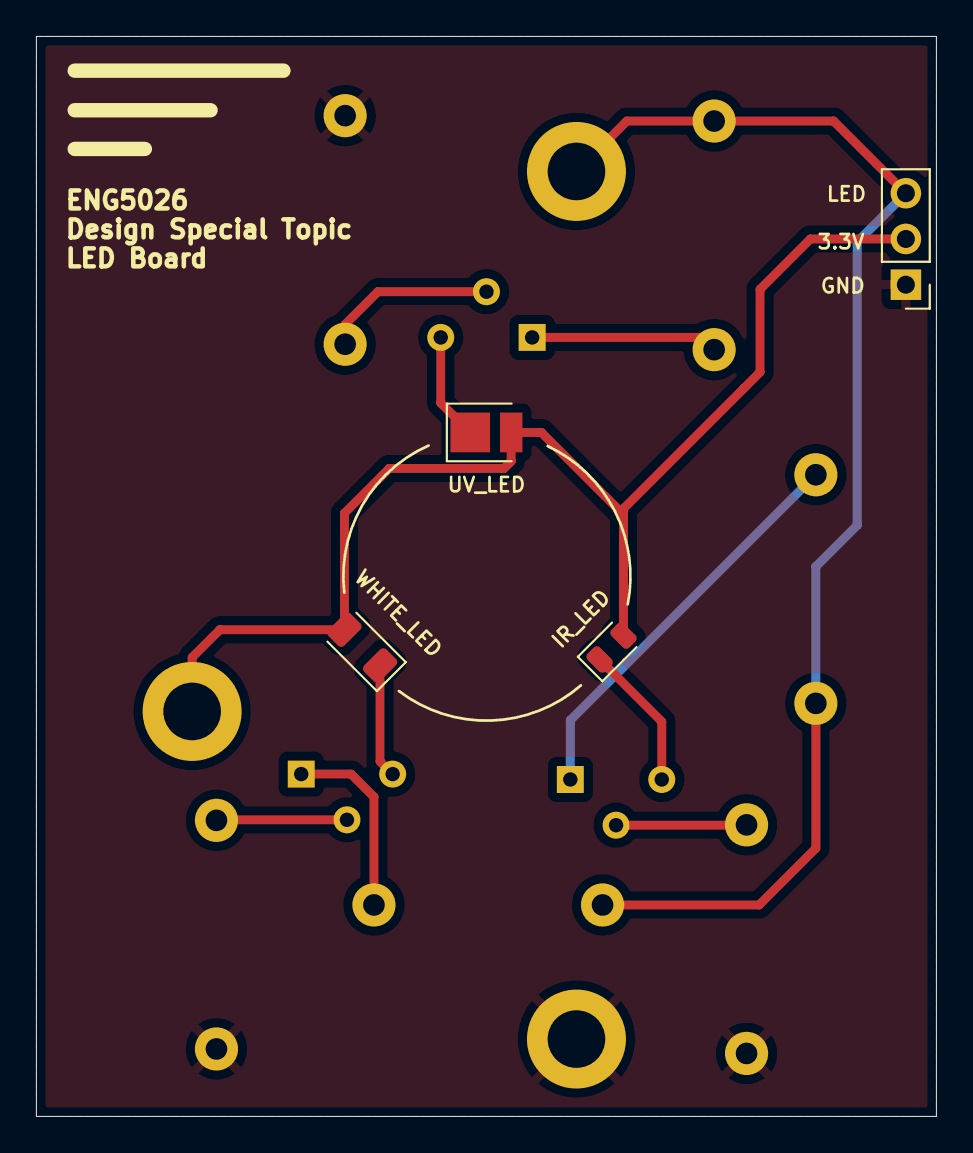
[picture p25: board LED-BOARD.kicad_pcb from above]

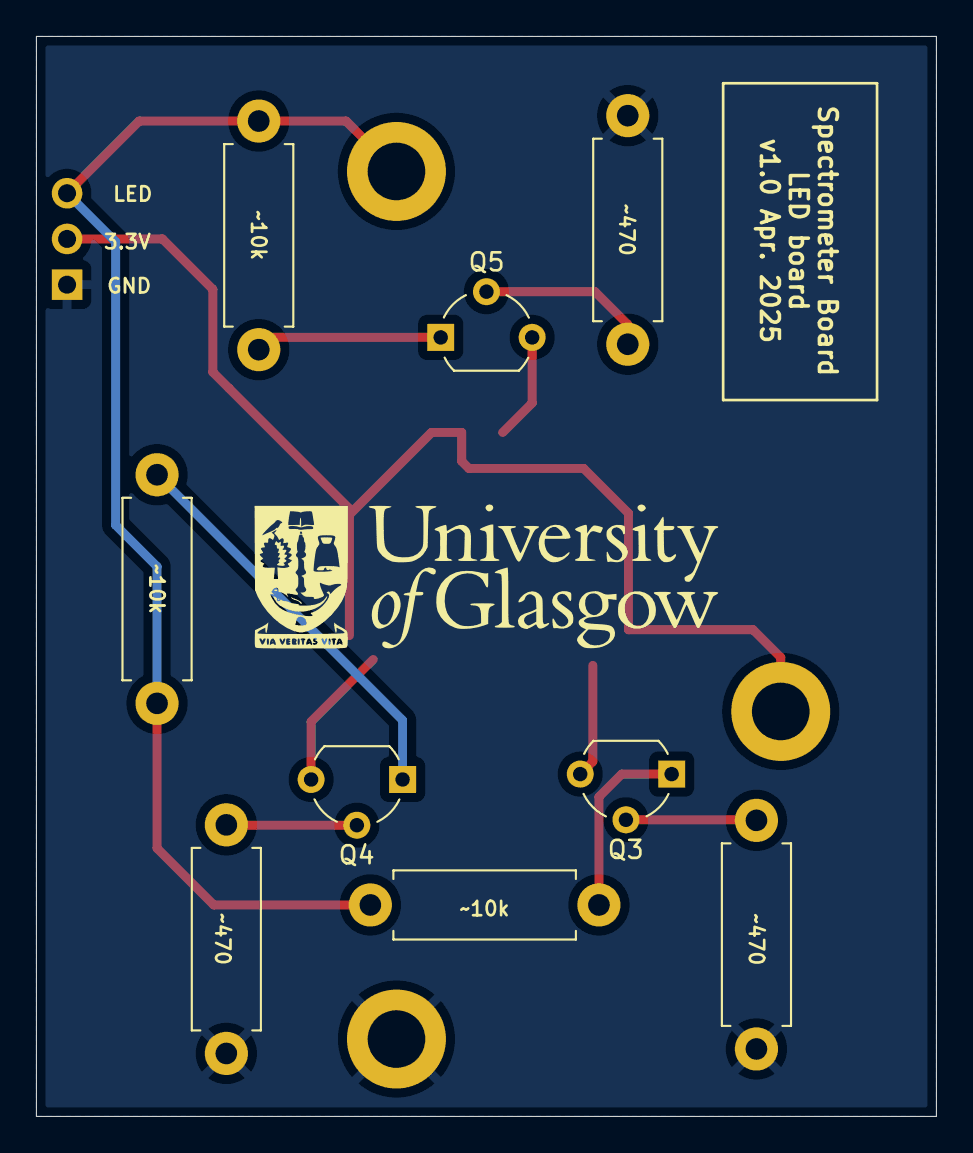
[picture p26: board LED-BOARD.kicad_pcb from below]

Board: 2 copper layers, 50.0 x 60.0 mm, 13 parts (9 on the bottom side), 12 nets.

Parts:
D4: WHITE-LED; LED_1206_3216Metric
D5: IR_LED; LED_0805_2012Metric
D6: UV_LED; LED_PLCC_2835
J8: LED->BOARD; PinHeader_1x03_P2.54mm_Vertical
Q3, Q4, Q5: Q_NPN_BEC; TO-92_Wide
R23, R24, R25: 10k; R_Axial_DIN0411_L9.9mm_D3.6mm_P12.70mm_Horizontal
R26, R27, R28: 470; R_Axial_DIN0411_L9.9mm_D3.6mm_P12.70mm_Horizontal

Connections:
+3.3V: D4.2 (A), D5.2 (A), D6.2 (A), J8.2
GND: J8.1, R26.1, R27.1, R28.1
LED-BOARD: J8.3, R23.1, R24.1, R25.1
unnamed: D4.1 (K), Q3.3 (C)
unnamed: D5.1 (K), Q4.3 (C)
unnamed: D6.1 (K), Q5.3 (C)
unnamed: Q3.1 (B), R23.2
unnamed: Q3.2 (E), R26.2
unnamed: Q4.1 (B), R24.2
unnamed: Q4.2 (E), R27.2
unnamed: Q5.1 (B), R25.2
unnamed: Q5.2 (E), R28.2

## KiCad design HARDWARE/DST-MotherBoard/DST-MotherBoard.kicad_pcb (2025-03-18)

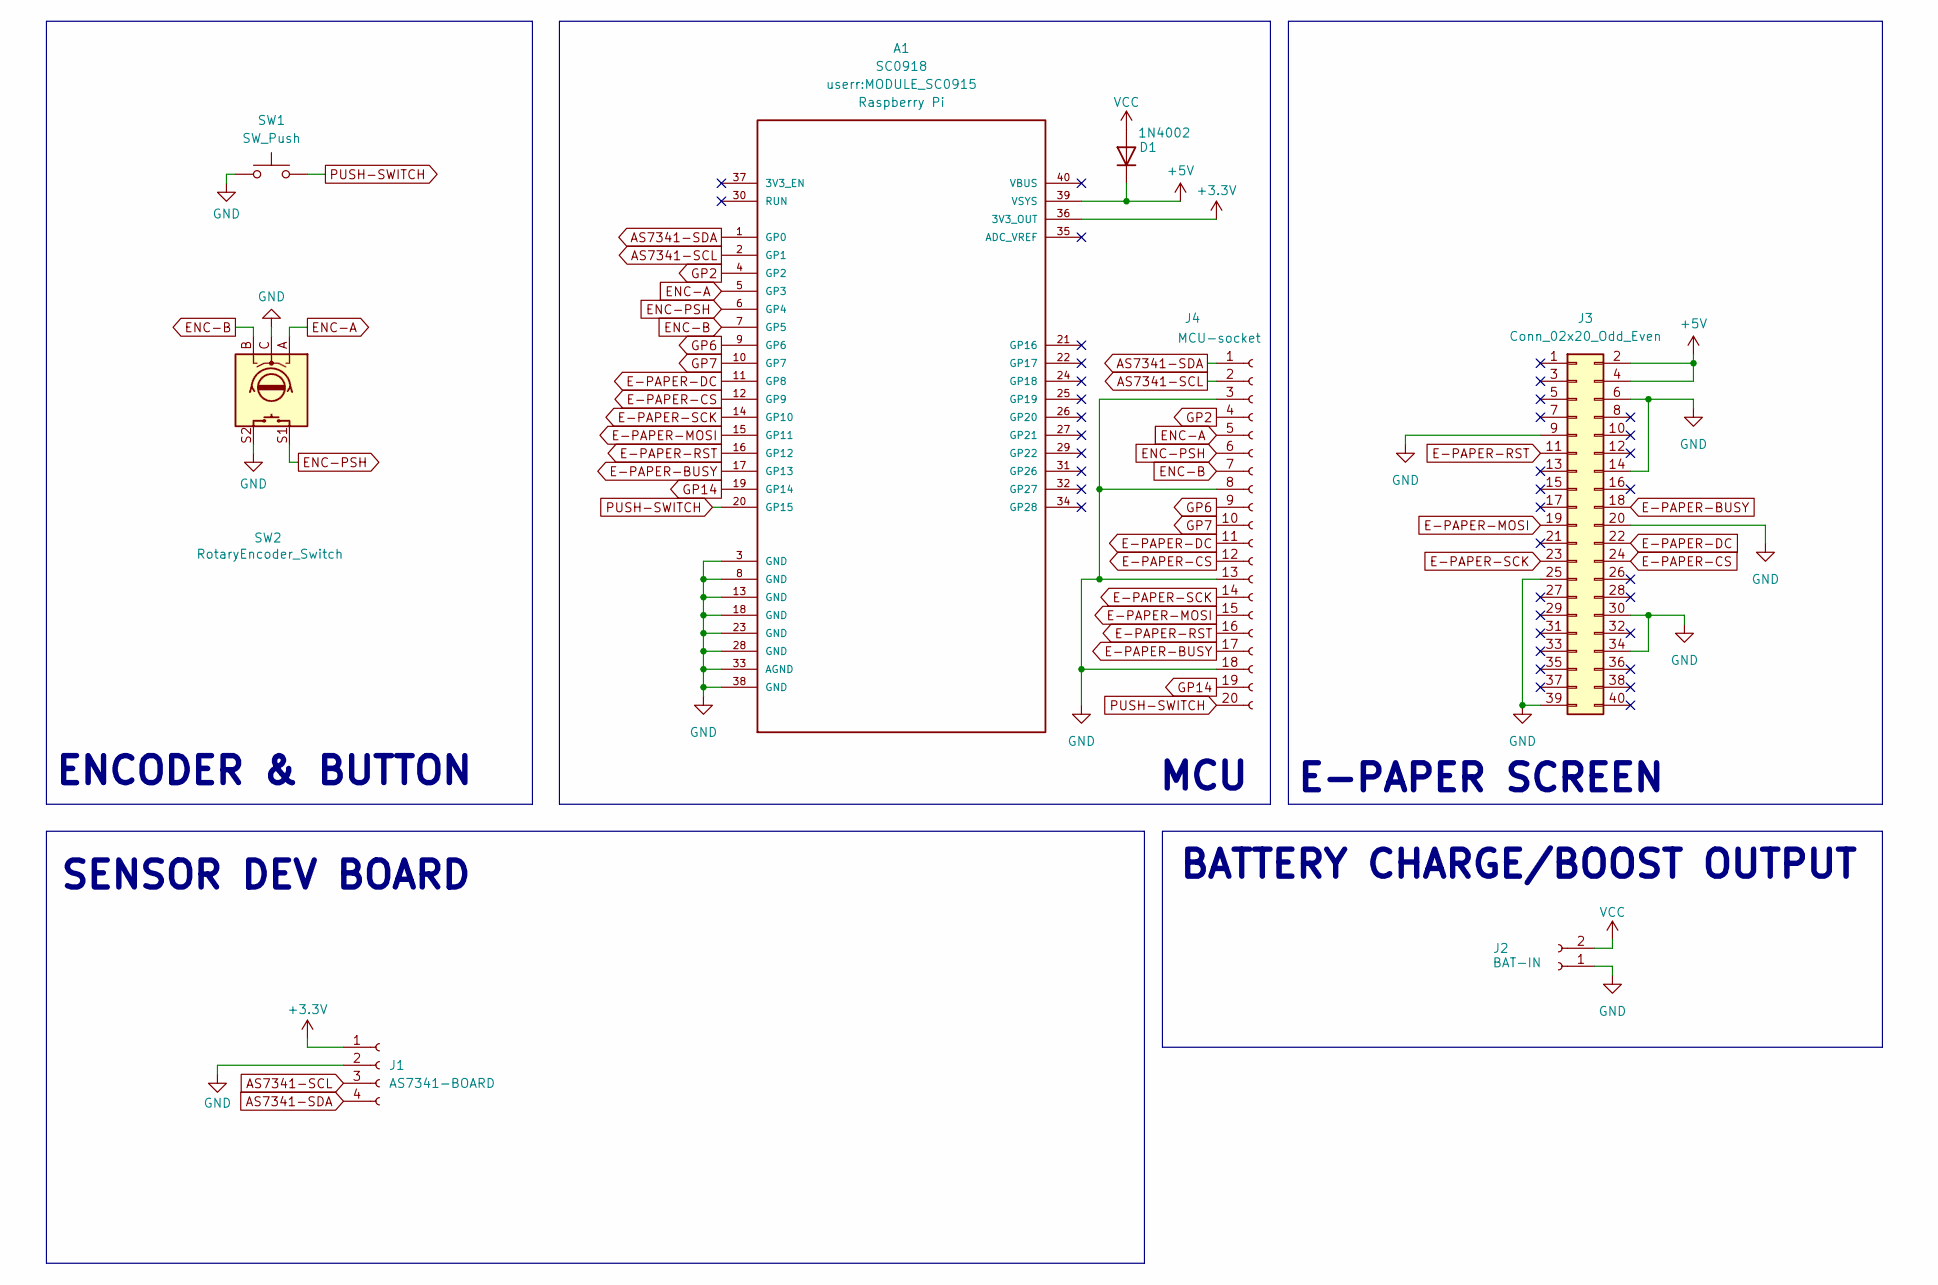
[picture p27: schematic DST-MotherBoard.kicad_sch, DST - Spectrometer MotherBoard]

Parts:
A1: SC0918; MODULE_SC0915; PARTREV 1.6
D1: 1N4002; D_DO-41_SOD81_P10.16mm_Horizontal; LCSC C169542
J1: AS7341-BOARD; PinSocket_1x04_P2.54mm_Vertical
J2: BAT-IN; PinSocket_1x02_P2.54mm_Vertical
J3: Conn_02x20_Odd_Even; PinSocket_2x20_P2.54mm_Vertical
J4: MCU-socket; PinHeader_1x20_P2.54mm_Vertical
SW1: SW_Push; SW_PUSH_6mm_H13mm
SW2: RotaryEncoder_Switch; RotaryEncoder_Alps_EC11E-Switch_Vertical_H20mm

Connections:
+3.3V: A1.36 (3V3_OUT), J1.1
+5V: A1.39 (VSYS), D1.1 (K), J3.2, J3.4
AS7341-SCL: A1.2 (GP1), J1.3, J4.2
AS7341-SDA: A1.1 (GP0), J1.4, J4.1
E-PAPER-BUSY: A1.17 (GP13), J3.18, J4.17
E-PAPER-CS: A1.12 (GP9), J3.24, J4.12
E-PAPER-DC: A1.11 (GP8), J3.22, J4.11
E-PAPER-MOSI: A1.15 (GP11), J3.19, J4.15
E-PAPER-RST: A1.16 (GP12), J3.11, J4.16
E-PAPER-SCK: A1.14 (GP10), J3.23, J4.14
ENC-A: A1.5 (GP3), J4.5, SW2.A
ENC-B: A1.7 (GP5), J4.7, SW2.B
ENC-PSH: A1.6 (GP4), J4.6, SW2.S1
GND: A1.3 (GND), A1.8 (GND), A1.13 (GND), A1.18 (GND), A1.23 (GND), A1.28 (GND), A1.33 (AGND), A1.38 (GND), J1.2, J2.1, J3.6, J3.9, J3.14, J3.20, J3.25, J3.30, J3.34, J3.39, J4.3, J4.8, J4.13, J4.18, SW1.1, SW2.C, SW2.S2
GP2: A1.4 (GP2), J4.4
GP6: A1.9 (GP6), J4.9
GP7: A1.10 (GP7), J4.10
GP14: A1.19 (GP14), J4.19
PUSH-SWITCH: A1.20 (GP15), J4.20, SW1.2
VCC: D1.2 (A), J2.2

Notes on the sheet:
E-PAPER SCREEN
ENCODER & BUTTON
MCU
SENSOR DEV BOARD
BATTERY CHARGE/BOOST OUTPUT

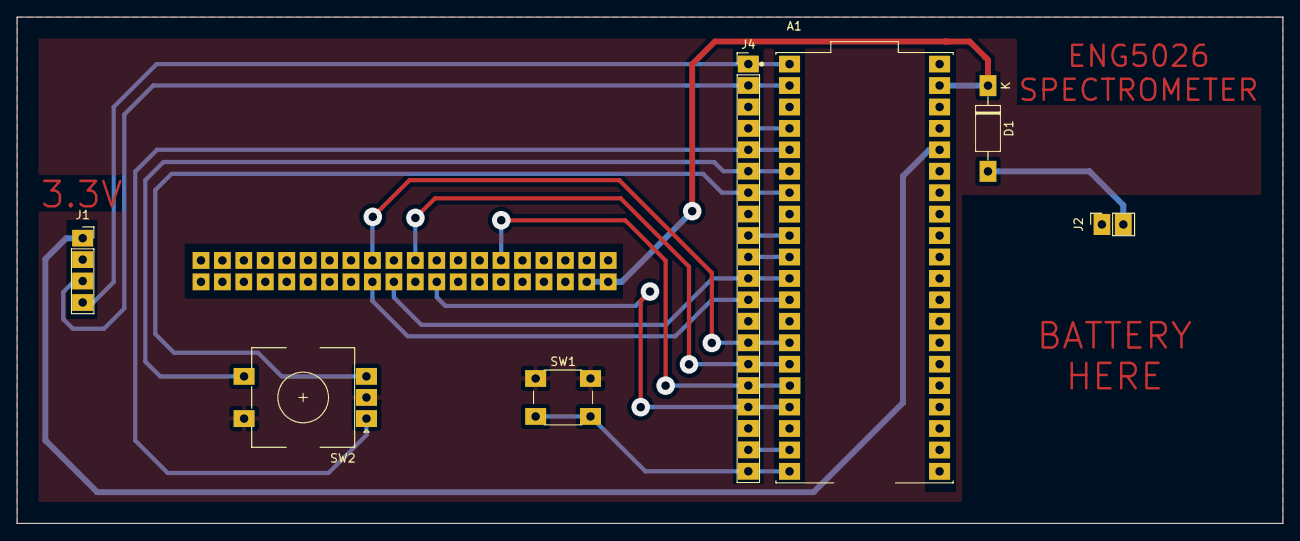
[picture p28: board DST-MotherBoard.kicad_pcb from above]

Board: 2 copper layers, 150.0 x 60.0 mm, 8 parts (1 on the bottom side), 20 nets.

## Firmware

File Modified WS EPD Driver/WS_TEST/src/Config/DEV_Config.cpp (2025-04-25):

/*****************************************************************************
* | File      	:   DEV_Config.c
* | Author      :   Waveshare team
* | Function    :   Hardware underlying interface
* | Info        :
*----------------
* |	This version:   V1.0
* | Date        :   2020-02-19
* | Info        :
#
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
******************************************************************************/
#include "DEV_Config.h"

void GPIO_Config(void)
{
    pinMode(EPD_BUSY_PIN,  INPUT);
    pinMode(EPD_RST_PIN , OUTPUT);
    pinMode(EPD_DC_PIN  , OUTPUT);
    pinMode(EPD_PWR_PIN  , OUTPUT);
    pinMode(EPD_CS_PIN , OUTPUT);
	// pinMode(EPD_SCK_PIN , OUTPUT);
	// pinMode(EPD_MOSI_PIN , OUTPUT);

    digitalWrite(EPD_PWR_PIN , HIGH);
    digitalWrite(EPD_CS_PIN , HIGH);
}

// void GPIO_Mode(UWORD GPIO_Pin, UWORD Mode)
// {
    // if(Mode == 0) {
        // pinMode(GPIO_Pin , INPUT);
	// } else {
		// pinMode(GPIO_Pin , OUTPUT);
	// }
// }
/******************************************************************************
function:	Module Initialize, the BCM2835 library and initialize the pins, SPI protocol
parameter:
Info:
******************************************************************************/
UBYTE DEV_Module_Init(void)
{
	//gpio
	GPIO_Config();

	//serial printf
	Serial.begin(115200);

	// spi
	SPI1.setCS(EPD_CS_PIN);
	SPI1.setSCK(EPD_SCK_PIN);
	SPI1.setTX(EPD_MOSI_PIN);
	SPI1.begin();
    SPI1.beginTransaction(SPISettings(4000000, MSBFIRST, SPI_MODE0));

	return 0;
}


// void DEV_GPIO_Init(void)
// {
    // SPI1.end(); 
    // pinMode(EPD_SCK_PIN, OUTPUT);
    // pinMode(EPD_MOSI_PIN, OUTPUT);
// }

// void DEV_SPI_Init(void)
// {
    // SPI1.setCS(EPD_CS_PIN);
	// SPI1.setSCK(EPD_SCK_PIN);
	// SPI1.setTX(EPD_MOSI_PIN);
	// SPI1.begin();
    // SPI1.beginTransaction(SPISettings(4000000, MSBFIRST, SPI_MODE0));
// }


/******************************************************************************
function:
			SPI read and write
******************************************************************************/
void DEV_SPI_WriteByte(UBYTE data)
{
    SPI1.transfer(data);
}

void DEV_SPI_Write_nByte(UBYTE *pData, UDOUBLE len)
{
    for (int i = 0; i < len; i++)
        DEV_SPI_WriteByte(pData[i]);
}

// void DEV_SPI_SendByte(UBYTE data)
// {
    // GPIO_Mode(EPD_MOSI_PIN, OUTPUT);
    // digitalWrite(EPD_CS_PIN, GPIO_PIN_RESET);
    // for (int i = 0; i < 8; i++)
    // {
        // if ((data & 0x80) == 0) digitalWrite(EPD_MOSI_PIN, GPIO_PIN_RESET); 
        // else                    digitalWrite(EPD_MOSI_PIN, GPIO_PIN_SET);

        // data <<= 1;
        // digitalWrite(EPD_SCK_PIN, GPIO_PIN_SET);     
        // digitalWrite(EPD_SCK_PIN, GPIO_PIN_RESET);
    // }
    // digitalWrite(EPD_CS_PIN, GPIO_PIN_SET);
// }

// UBYTE DEV_SPI_ReadByte()
// {
    // UBYTE j=0xff;
    // GPIO_Mode(EPD_MOSI_PIN, INPUT);
    // digitalWrite(EPD_CS_PIN, GPIO_PIN_RESET);
    // for (int i = 0; i < 8; i++)
    // {
        // j = j << 1;
        // if (digitalRead(EPD_MOSI_PIN))  j = j | 0x01;
        // else                            j = j & 0xfe;
        
        // digitalWrite(EPD_SCK_PIN, GPIO_PIN_SET);     
        // digitalWrite(EPD_SCK_PIN, GPIO_PIN_RESET);
    // }
    // digitalWrite(EPD_CS_PIN, GPIO_PIN_SET);
    // GPIO_Mode(EPD_MOSI_PIN, 1);
    // return j;
// }




void DEV_Module_Exit(void)
{
    digitalWrite(EPD_PWR_PIN , LOW);
}

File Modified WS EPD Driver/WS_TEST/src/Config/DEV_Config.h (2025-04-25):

/*****************************************************************************
* | File      	:   DEV_Config.h
* | Author      :   Waveshare team
* | Function    :   Hardware underlying interface
* | Info        :
*----------------
* |	This version:   V1.0
* | Date        :   2020-02-19
* | Info        :
#
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
******************************************************************************/
#ifndef _DEV_CONFIG_H_
#define _DEV_CONFIG_H_

#include <Arduino.h>
#include <stdint.h>
#include <stdio.h>
#include <SPI.h>

/**
 * data
**/
#define UBYTE   uint8_t
#define UWORD   uint16_t
#define UDOUBLE uint32_t

/**
 * GPIO config
**/
// #define EPD_SCK_PIN     13
// #define EPD_MOSI_PIN    11
// #define EPD_CS_PIN      10
// #define EPD_DC_PIN      9
// #define EPD_RST_PIN     8
// #define EPD_BUSY_PIN    7
// #define EPD_PWR_PIN     6

#define EPD_SCK_PIN     10
#define EPD_MOSI_PIN    11
#define EPD_CS_PIN      9
#define EPD_DC_PIN      8
#define EPD_RST_PIN     12
#define EPD_BUSY_PIN    13
#define EPD_PWR_PIN     6

#define GPIO_PIN_SET   1
#define GPIO_PIN_RESET 0

/**
 * GPIO read and write
**/
#define DEV_Digital_Write(_pin, _value) digitalWrite(_pin, _value == 0? LOW:HIGH)
#define DEV_Digital_Read(_pin) digitalRead(_pin)

/**
 * delay x ms
**/
#define DEV_Delay_ms(__xms) delay(__xms)

/*------------------------------------------------------------------------------------------------------*/
UBYTE DEV_Module_Init(void);
void DEV_GPIO_Init(void);
void DEV_SPI_Init(void);

void GPIO_Mode(UWORD GPIO_Pin, UWORD Mode);
void DEV_SPI_WriteByte(UBYTE data);
void DEV_SPI_SendByte(UBYTE data);
UBYTE DEV_SPI_ReadByte();
void DEV_SPI_Write_nByte(UBYTE *pData, UDOUBLE len);
void DEV_Module_Exit(void);
#endif

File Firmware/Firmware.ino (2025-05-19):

#include "spectroscopico.h"

#define PIN_IN1 5
#define PIN_IN2 3

Adafruit_AS7341 as7341;
AS7265X sensor;
RotaryEncoder *encoder = nullptr;
GxEPD2_DISPLAY_CLASS<GxEPD2_DRIVER_CLASS, MAX_HEIGHT(GxEPD2_DRIVER_CLASS)> display(GxEPD2_DRIVER_CLASS(/*CS=*/ 9, /*DC=*/ 8, /*RST=*/ 12, /*BUSY=*/ 13)); // Waveshare Pico-ePaper-2.9
SPIClassRP2040 SPIn(spi1, -1, 13, 10, 11);

void setup() {
  //for RNG of sensor data, disable if not required
  randomSeed(analogRead(A0));

  //button interrupt
  pinMode(LED_BUILTIN, OUTPUT);
  pinMode(15, INPUT_PULLUP);
  attachInterrupt(digitalPinToInterrupt(15), handleBTNINT, FALLING);

  //display initialisation
  display.epd2.selectSPI(SPIn, SPISettings(4000000, MSBFIRST, SPI_MODE0));
  display.init(115200, true, 10, false, SPIn, SPISettings(4000000, MSBFIRST, SPI_MODE0));
  //full refresh to begin
  display.clearScreen();

  //encoder initialisation
  encoder = new RotaryEncoder(PIN_IN1, PIN_IN2, RotaryEncoder::LatchMode::FOUR3);
  attachInterrupt(digitalPinToInterrupt(PIN_IN1), checkPosition, CHANGE);
  attachInterrupt(digitalPinToInterrupt(PIN_IN2), checkPosition, CHANGE);
  
  //spectrometer initialisation
  pinMode(0, OUTPUT); //SDA
  pinMode(1, OUTPUT); //SCL
  pinMode(16, OUTPUT); //EXTERNAL LED ENABLE
  Wire.setSCL(1);
  Wire.setSDA(0);
  delay(750); //750ms gives E-Paper enough time to initialise
  if (sensor.begin() == true){ //first check for AS7265x
    sensecon = 1;
    bigText(false, "AS7265x Connected");
    sensor.disableIndicator();
  }
  else if (as7341.begin() == true){ //if no AS7265x then check for AS7341
    sensecon = 2;
    bigText(false, "AS7341 Connected");
    as7341.setATIME(100);
    as7341.setASTEP(999);
    as7341.setGain(AS7341_GAIN_256X);
    as7341.setLEDCurrent(20); //mA
  }
  else{
    sensecon = 0;
    bigText(false, "No Sensor Detected");
  }
  delay(1000);
  drawEmpty(false, "Booted");
}


void loop() {

  if (buttonpress) {
    Serial.print("LOOP: buttonpress TRUE. Current 'measuring': "); Serial.println(measuring); // DEBUG
    buttonpress = false; // Consume the flag *immediately*

    if (measuring) {
      // If currently measuring, this press means STOP.
      measuring = false; // Signal the currently running multimeasure to stop.
      Serial.println("LOOP: Set 'measuring' to FALSE (requesting stop).");
      // multimeasure's internal 'while(measuring)' should catch this.
      // No need to call multimeasure() again here.
      // The screen update to "Stopped" or "Ready" will happen after multimeasure returns.
    } else {
      // Not measuring, so this press means START.
      measuring = true;
      Serial.print("LOOP: Set 'measuring' to TRUE (requesting start). Mode: "); Serial.println(sensemode);

      multimeasure(); // Call the function. It will perform its action(s).
                      // For continuous/burst, it loops internally until 'measuring' is false.

      // After multimeasure() returns (it completed, or was stopped by 'measuring' becoming false):
      Serial.println("LOOP: multimeasure() has returned.");
      measuring = false; // Ensure state is consistently 'not measuring' after any operation.

      // Update display to reflect the end of operation.
      // If multimeasure showed results for single/burst, that's fine.
      // If continuous was stopped, or any mode finished, show "Ready".
      drawEmpty(false, "Ready");
    }
  }

  rp2040.idleOtherCore();
  delay(20); // A small delay is good practice.
}

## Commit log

2025-03-18 added MotherBoard Files
    [DST-MotherBoard.kicad_pcb, DST-MotherBoard.kicad_sch]
2025-03-18 added arduino code
2025-04-01 I2C works + Prints values
2025-04-08 New Custom Board
    created the KiCad file and started with schematic
    [Embedded-Board.kicad_pcb, Embedded-Board.kicad_sch, POWER.kicad_sch, RP2040.kicad_sch]
2025-04-08 Schematic v1 done
    [Embedded-Board.kicad_sch, POWER.kicad_sch, RP2040.kicad_sch]
2025-04-08 small fix
    [Embedded-Board.kicad_sch, RP2040.kicad_sch]
2025-04-13 Added modified epd driver
    Modified EPD arduino firmware from waveshare to work with the pinout on pi pico. Original repo is https://github.com/waveshareteam/e-Paper
2025-04-14 Removed unnecessary files
    now builds if you add "src" to an arduino sketch directory
2025-04-25 New PCB design for JLCPCB
    [AS7341.kicad_pcb, AS7341.kicad_sch, AS7341.step, Embedded-Board.kicad_pcb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]
2025-04-25 small update
    [Embedded-Board.kicad_pcb]
2025-04-27 C++ for visualisation using AS7265x
    This is the program used to visualise readings from the AS7265x sensor in the form of a bar chart.
2025-04-29 Final PCB version
    [BOM-Spectrometer-v1_0.csv, CENTROID-Spectrometer-v1_0.csv, Embedded-Board-B_Cu.gbl, Embedded-Board-B_Mask.gbs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]
2025-04-29 Splitting the Embedded & LED PCBs
    [Embedded-Board-B_Cu.gbl, Embedded-Board-B_Mask.gbs, Embedded-Board-B_Silkscreen.gbo, Embedded-Board-Edge_Cuts.gm1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]
2025-04-29 updated BOM
    [BOM-Spectrometer-v1_0.csv]
2025-04-29 Board Pictures for the Blog Post
    [Embedded-Board.kicad_pcb, LED-BOARD.kicad_pcb]
2025-05-02 Added encoder and button support
    Now detects when the sensor is connected and shows this on screen at startup.
    Encoder changes between firemode (single, continuous, burst (2-9)). When rotated while switch is pressed, changes LED mode (combinations of internal and external on/off).
    Button will trigger a reading but haven't bound interrupt yet.
2025-05-09 Created new Firmware
    Changes most of how things work, can't comment on sensor compatibility yet but should be easier to understand. Encoder doesn't register yet and for some reason pressing the button takes two readings 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
    Still don't know exactly how to do the averaging but shouldn't be hard, and this uses full refreshes for everything but it's fast enough. This might need to change for the encoder though.
2025-05-16 AS7431 Working
    Added new screen for displaying results from AS7341, automatically sets based on which sensor is detected. Input issues remain and the colour detection hasn't been updated for AS7341 yet.
2025-05-16 3D CASE - v1
    [Embedded-Board.kicad_pcb, embedded-case-bottom-v1.stl, embedded-case-sensor-v1.stl, embedded-case-top-v1.stl]
2025-05-20 continuous mode attempt
    the issue now is that the timer does not enable itself when it is supposed to, nor does it disable itself when force enabled.
    [embedded-case-top-v1.3mf]
2025-05-21 fixed ripeness function, disabled UV LED
